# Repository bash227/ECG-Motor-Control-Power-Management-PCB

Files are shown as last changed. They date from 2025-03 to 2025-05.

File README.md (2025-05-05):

# ECG-Integrated Motor Control PCB  
**Final Project for BME405 - Introduction to Design of Medical Electronic Devices**  
*Ankara University, Department of Biomedical Engineering*  

---

## Project Overview  
A multi-functional PCB combining:  
- **ECG Signal Acquisition** (INA188 instrumentation amplifier, 0.5Hz-100Hz bandwidth)  
- **Power Management** (3.6V Li-ion charging, ±5V/12V regulation)  
- **Motor/Actuator Control** (BD6220F-E2 driver, relay circuits)  

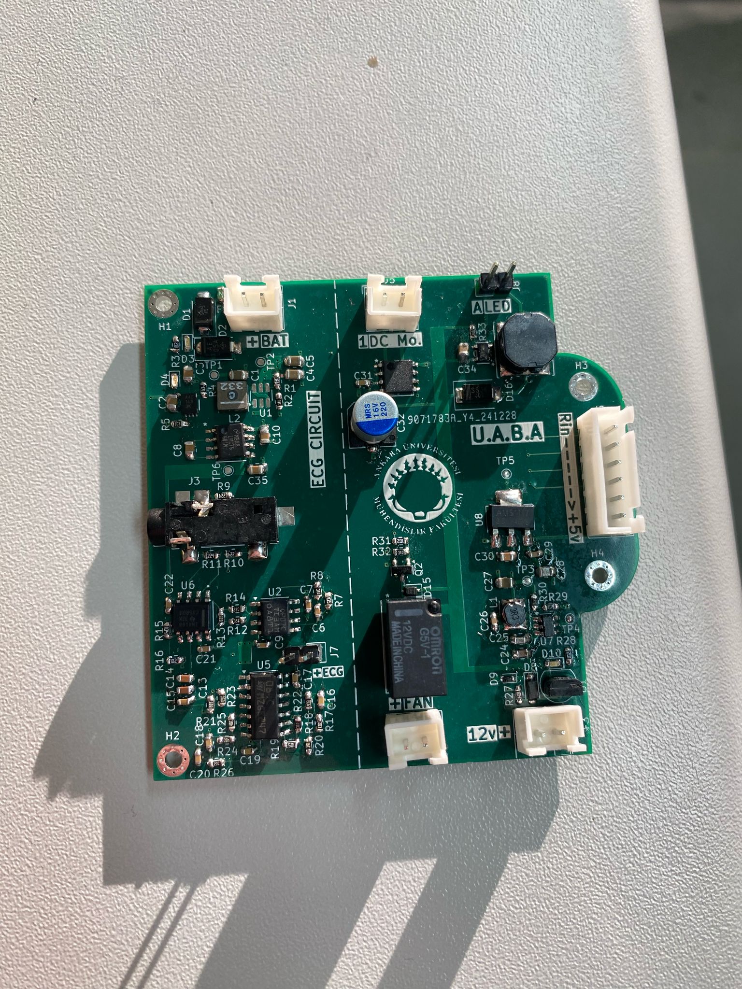
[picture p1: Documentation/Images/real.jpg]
PCB 3D Render


---

## Team Members  
| Name              | Role                                  |  
|-------------------|---------------------------------------|  
| [bash227](https://github.com/bash227)| PCB Layout              |  
| [UmutAygun](https://github.com/UmutAygun)| Schematic Design          |  

---

## Repository Structure  
```plaintext
ECG_Motor_PCB/
├── Hardware/ 
│   │   
│   ├── Outputs/
│   └── 3D models/
├── Documentation/
└── README.md
```

## Key Features
### Power managment
- MCP73831 Li-ion charger (0.5A)
- TLV61070A boost converter (3.6V→5V)
- LMC7660 voltage inverter (+5V→-5V)

### ECG Frontend
- INA188 instrumentation amplifier (G=10)
- 0.05Hz high-pass filter
- 50Hz notch filter

### Motor Control
- BD6220F-E2 DC motor driver
- AP8803WTG-7 LED driver
- Optoisolated relay control
---
##  Setup Guide
1. Clone the repository:
```bash
git clone https://github.com/yourusername/ECG-Motor-Control-PCB.git
```
2. Open in KiCad:
```bash
PCB_FINAL_UPDATED.kicad_pro
```
3. Set 3D model path in KiCad:
```bash
KICAD8_3DMODEL_DIR = ${KIPRJMOD}/Hardware/3D_Models
```
## Academic Information
- Course: BME405 - Introduction to Medical Electronics Design
- Institution: Ankara University

## License

This project is licensed under the **MIT License** - see the [LICENSE](LICENSE) file for details.

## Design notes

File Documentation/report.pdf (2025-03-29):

### 1- Soldiered circuit

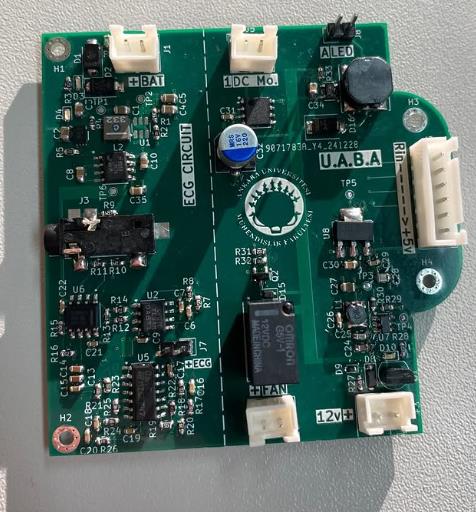
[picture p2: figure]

### 2- PCB design

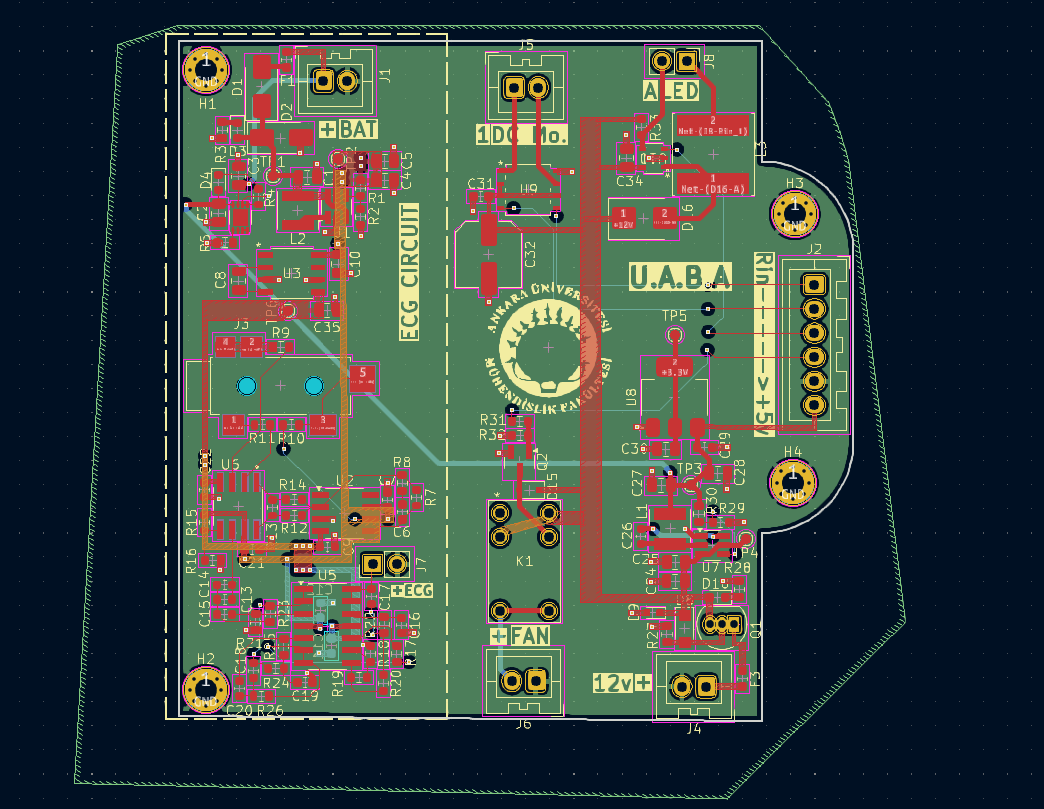
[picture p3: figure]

### 3- Schematics a- Analog circuit’s protection and regulators

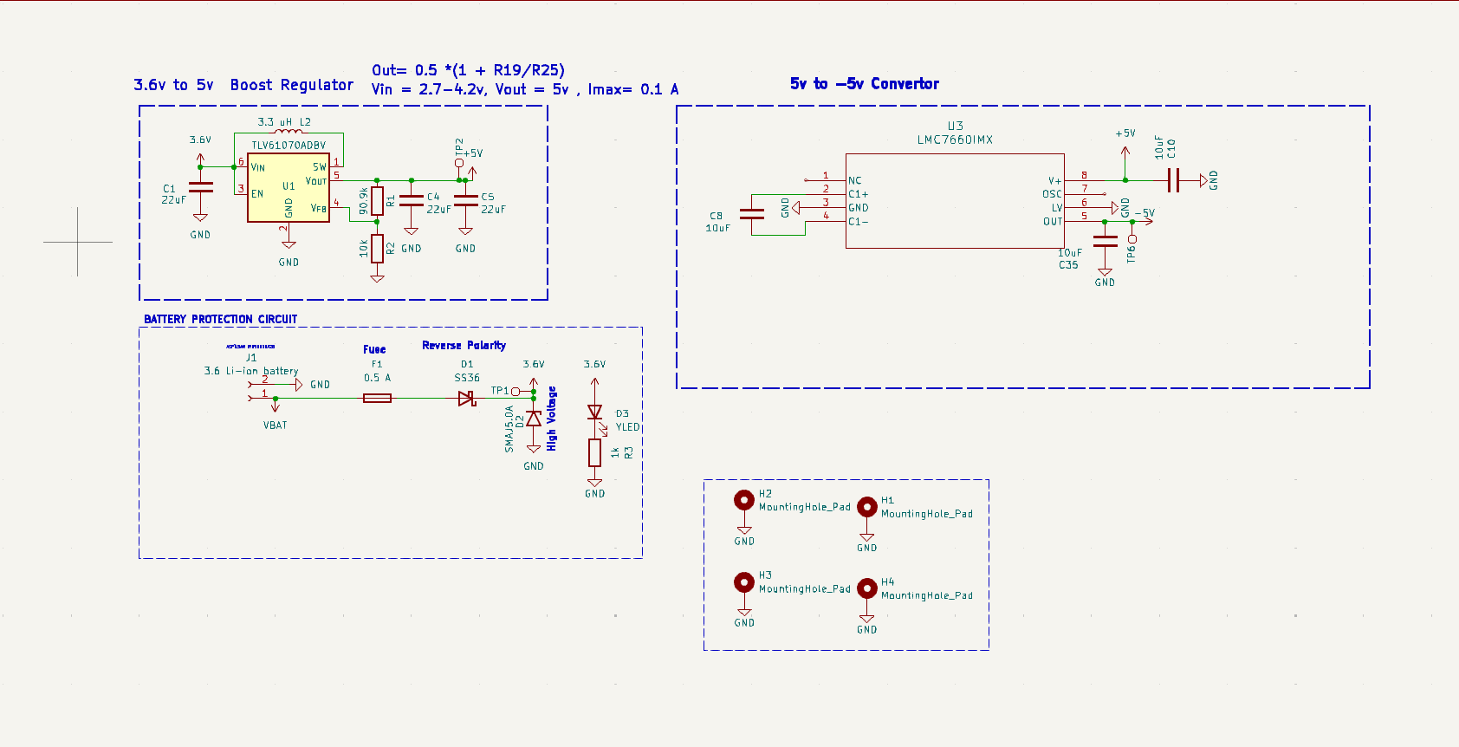
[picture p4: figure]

The battery will provide 3.6v, at first there is high current protection (F1) , reverse polarity protection (D1) and high voltage protection (D2), then the 3.6v is boosted to 5v using boost regulator (TLV61070ADBV) and the output voltage is controlled using 2 resistors (R2, R1) by using the values in the formula in the picture, because of the low values of the ECG, -5v have to be provided to the negative

### voltage pin of the amplifiers, and it’s supplied by another regulator (LMC7660IMX

### b- ECG signal amplifying circuit

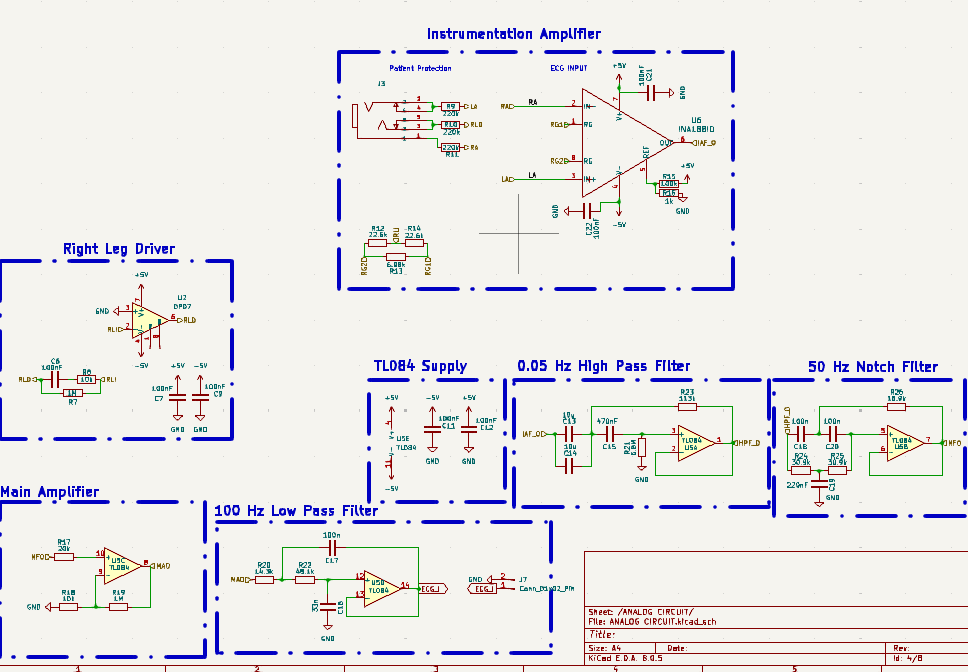
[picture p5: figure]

### Before the amplifying patient protection (using high resistance resistors to minimize the

current) and right leg driver (to eliminate the body’s noise ) are done. With a 10 gain the signal is amplified using the instrumentational amplifier (INA188ID), after that the signal is filtered by a 0.5Hz high pass filter and 50Hz notch filter, then the main amplifier amplifies the signal by a gain of 100, finally the signal is filtered using 100Hz low pass filter.

### c- Charger circuit

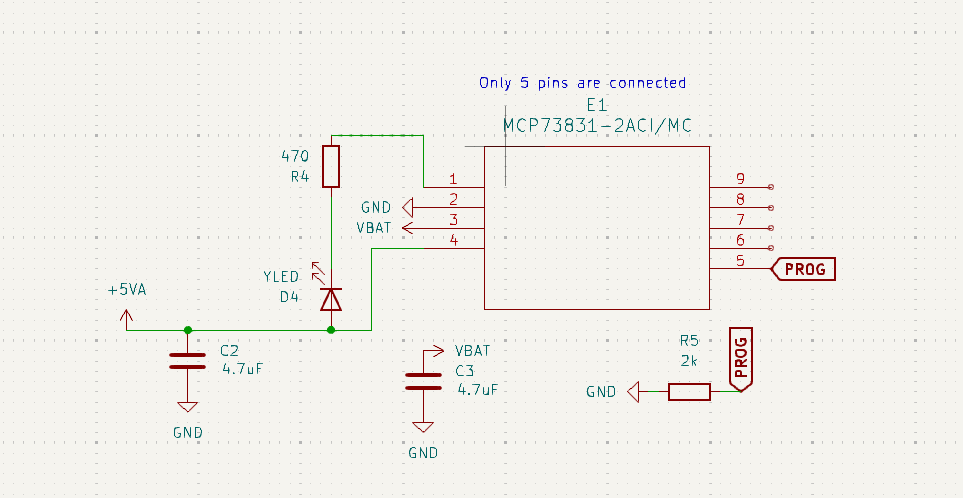
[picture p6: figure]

### To charge the battery with a charge module (MCP73831-2ACI/MC) with a 0.5A charging

current.

### d- High voltage protection and regulation circuit

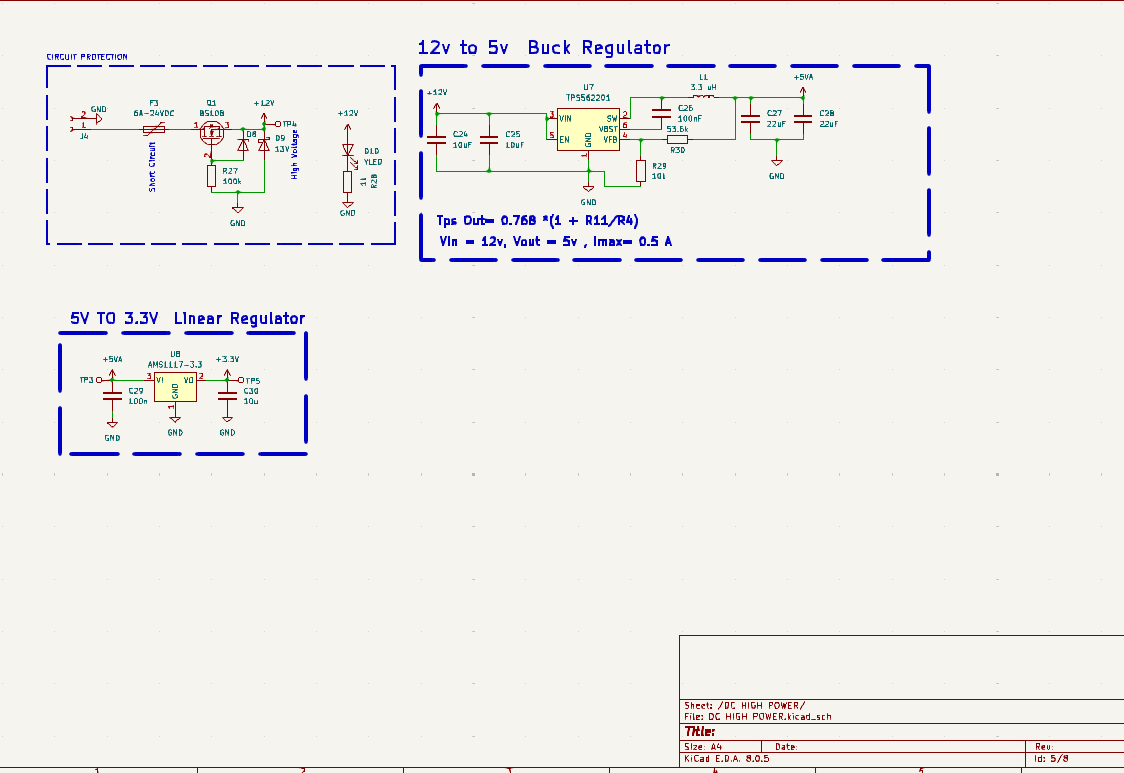
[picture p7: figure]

For the high voltage section same protection is done but due to the high current for reverse polarity protection transistor is done instead of Schottky diode. After that the 12v dc voltage is regulated to 5v using buck regulator (TPS562201), after that the 5v is regulated to 3.3v using linear regulator (AMS1117-3.3).

### e- DC motor driver and control connector

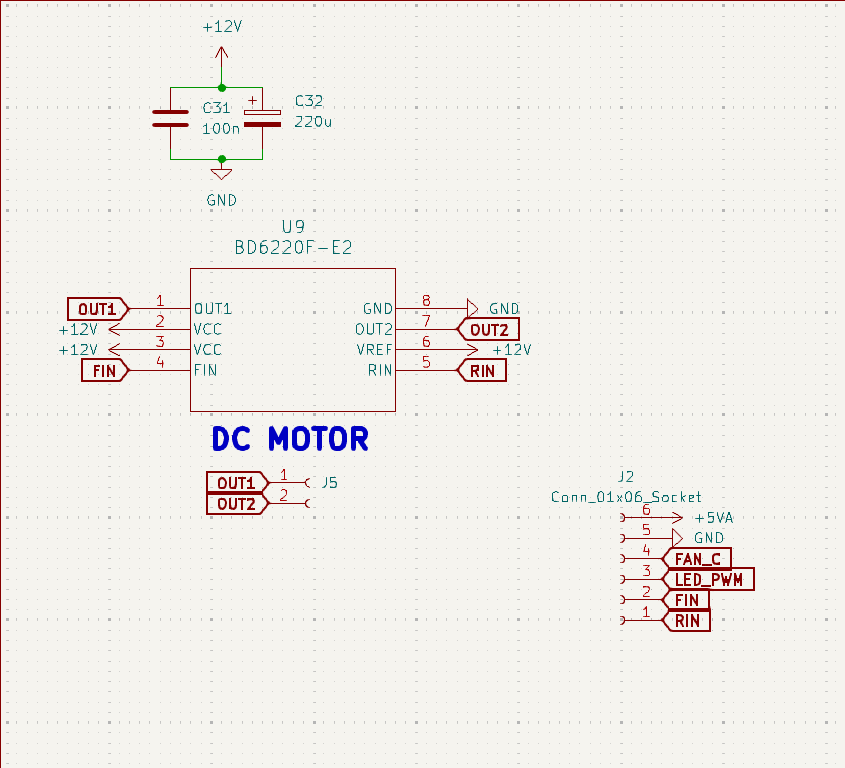
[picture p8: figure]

In here there is a dc motor driver (BD6220F-E2) and 2 decoupling capacitors connected to it, its supplied with 12v for motor supply, and the motors will be connected to OUT1 and OUT2 pins.

For the control connector there is 5v output to test the circuit and other pins for the other components control.

### f- Fan control circuit

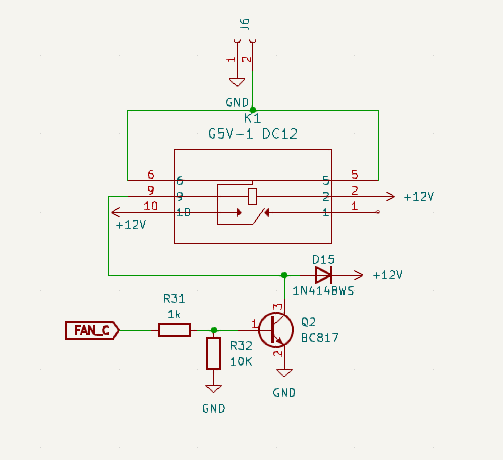
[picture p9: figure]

A relay is used with a transistor to control the fan, and a diode to block the current that is stored in the coil in the relay, and its controlled using the FAN_C pin in the control connector.

### g- Led driver circuit

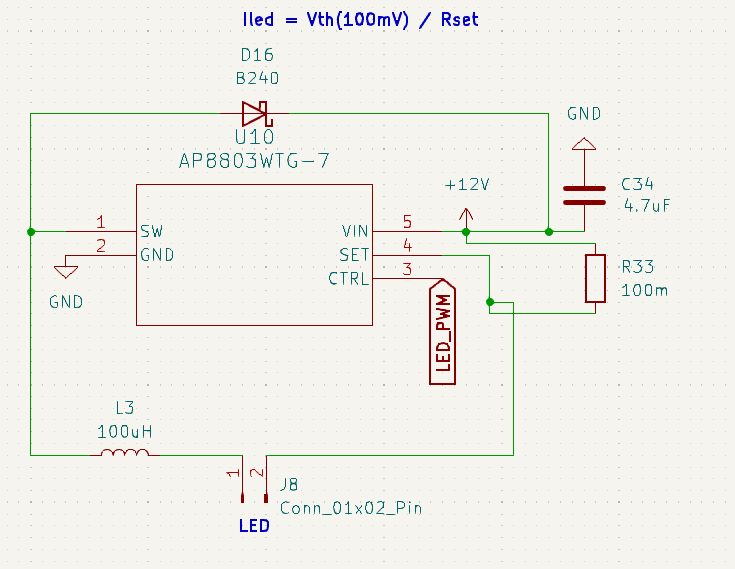
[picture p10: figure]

A led driver to control (AP8803WTG-7) the LED driver is supplied with 12v and the current is set using the R33 value so the LED current in this circuit is 1A.

### 4- BOM list

null | References | Value | Footprint | Quantity | LINK
1 | C6, C7, C9, C11, C12, C17, C18, C20, C21, C22, C26, C29, C31 | 100nF | C_0603_1608Metric | 13 | https://ozdisan.com/Product/Detail/476015/C C0603KRX7R9BB104 (https://ozdisan.com/Product/Detail/476015/CC0603KRX7R9BB104)
2 | C8, C10, C24, C25, C30, C35 | 10uF | C_0805_2012Metric | 6 | https://ozdisan.com/p/57?ids=9695;452010,9697;356027&groupids=9695,9697&propids=452010,356027&SearchText=10uf&sayfaAdedi=20
3 | C1, C4, C5, C27, C28 | 22uF | C_0805_2012Metric | 5 | https://ozdisan.com/pasif-komponentler/kapasitorler/smt-smd-ve-mlcc-kapasitorler/CL21A226MPCLRNC/522719 (https://ozdisan.com/pasif-komponentler/kapasitorler/smt-smd-ve-mlcc-kapasitorler/CL21A226MPCLRNC/522719)
4 | C2, C3, C34 | 4.7uF | C_0805_2012Metric | 3 | https://ozdisan.com/pasif-komponentler/kapasitorler/smt-smd-ve-mlcc-kapasitorler/CL21A226MPCLRNC/522719
5 | C13, C14 | 10u | C_0603_1608Metric | 2 | https://ozdisan.com/pasif-komponentler/kapasitorler/smt-smd-ve-mlcc-kapasitorler/GRT188C81C106ME13D/732963
6 | C15 | 470nF | C_0603_1608Metric | 1 | https://ozdisan.com/pasif-komponentler/kapasitorler/smt-smd-ve-mlcc-kapasitorler/CL10B474KA8NNNC/355575
7 | C16 | 33n | C_0603_1608Metric | 1 | https://ozdisan.com/pasif-komponentler/kapasitorler/smt-smd-ve-mlcc-kapasitorler/CL10B333KB8NNNC/26341
8 | C19 | 220nF | C_0603_1608Metric | 1 | CL10B224KO8NNNC (https://ozdisan.com/pasif-komponentler/kapasitorler/smt-smd-ve-mlcc-kapasitorler/CL10B224KO8NNNC/14442)
9 | C32 | 220u | C_Elec_6.3x7.7 | 1 | CD010M221E7DPKKKV00A ,
10 | R2, R8, R18, R29, R32 | 10K | R_0603_1608Metric | 5 | CRT03F7E1002 (https://ozdisan.com/pasif-komponentler/direncler/smt-smd-ve-cip-direncler/CRT03F7E1002/1054351)
11 | R3, R16, R28, R31 | 1k | R_0603_1608Metric | 4 | CRT03J7E1001 (https://ozdisan.com/pasif-komponentler/direncler/smt-smd-ve-cip-direncler/CRT03J7E1001/1054377)
12 | R9, R10, R11 | 220k | R_0603_1608Metric | 3 | RC0603JR-07220KL (https://ozdisan.com/pasif-komponentler/direncler/smt-smd-ve-cip-direncler/RC0603JR-07220KL/834868)
13 | R7, R19 | 1M | R_0603_1608Metric | 2 | RC0603JR-071ML (https://ozdisan.com/pasif-komponentler/direncler/smt-smd-ve-cip-direncler/RC0603JR-071ML/403066)
14 | R12, R14 | 22.6k | R_0603_1608Metric | 2 | 0603SAF2262T5E (https://ozdisan.com/pasif-komponentler/direncler/smt-smd-ve-cip-direncler/0603SAF2262T5E/505927)
15 | R15, R27 | 100k | R_0603_1608Metric | 2 | RC0603JR-07100KL (https://ozdisan.com/pasif-komponentler/direncler/smt-smd-ve-cip-direncler/RC0603JR-07100KL/497416)
16 | R24, R25 | 30.9k | R_0603_1608Metric | 2 | 0603SAF3092T5E (https://ozdisan.com/pasif-komponentler/direncler/smt-smd-ve-cip-direncler/0603SAF3092T5E/467401)
17 | R1 | 90.9k | R_0603_1608Metric | 1 | RC0603FR-0790K9L (https://ozdisan.com/pasif-komponentler/direncler/smt-smd-ve-cip-direncler/RC0603FR-0790K9L/618083)
18 | R4 | 470 | R_0603_1608Metric | 1 | RC0603JR-07470RL (https://ozdisan.com/pasif-komponentler/direncler/smt-smd-ve-cip-direncler/RC0603JR-07470RL/387456)
19 | R5 | 2k | R_0603_1608Metric | 1 | 0603SAJ0202T5E (https://ozdisan.com/pasif-komponentler/direncler/smt-smd-ve-cip-direncler/0603SAJ0202T5E/338094)
20 | R13 | 6.98k | R_0603_1608Metric | 1 | 0603SAF6981T5E (https://ozdisan.com/pasif-komponentler/direncler/smt-smd-ve-cip-direncler/0603SAF6981T5E/505901)
21 | R17 | 20k | R_0603_1608Metric | 1 | 0603SAJ0203T5E (https://ozdisan.com/pasif-komponentler/direncler/smt-smd-ve-cip-direncler/0603SAJ0203T5E/349000)
22 | R20 | 14.3k | R_0603_1608Metric | 1 | 0603SAF1432T5E (https://ozdisan.com/pasif-komponentler/direncler/smt-smd-ve-cip-direncler/0603SAF1432T5E/505915)
23 | R21 | 6.8M | R_0603_1608Metric | 1 | 0603SAF6804T5E (https://ozdisan.com/pasif-komponentler/direncler/smt-smd-ve-cip-direncler/0603SAF6804T5E/602901)
24 | R22 | 48.1k | R_0603_1608Metric | 1 | CRT03F7E4702 47k (https://ozdisan.com/pasif-komponentler/direncler/smt-smd-ve-cip-direncler/CRT03F7E4702/1054352)
25 | R23 | 113k | R_0603_1608Metric | 1 | 0603SAF1133T5E (https://ozdisan.com/pasif-komponentler/direncler/smt-smd-ve-cip-direncler/0603SAF1133T5E/505968)
26 | R26 | 16.9k | R_0603_1608Metric | 1 | 0603WGF1692T5E (https://ozdisan.com/pasif-komponentler/direncler/smt-smd-ve-cip-direncler/0603WGF1692T5E/335214)
27 | R30 | 53.6k | R_0603_1608Metric | 1 | 0603SAF5362T5E (https://ozdisan.com/pasif-komponentler/direncler/smt-smd-ve-cip-direncler/0603SAF5362T5E/454292)
28 | R33 | 100m | R_0603_1608Metric | 1 | 0603SAF100LT5E (https://ozdisan.com/pasif-komponentler/direncler/smt-smd-ve-cip-direncler/0603SAF100LT5E/456321)
29 | L1 | 3.3 uH | L_Wurth_WE-LQSH-4020 | 1 | FPI0302-3R3M
30 | L2 | 3.3 uH | L_Abracon_ASPI-4030S | 1 | XFL4020-332MEC
31 | L3 | 100uH | L_Changjiang_FNR8040S | 1 | SRN8040-101M
32 | D3, D4, D10 | YLED | LED_0603_1608Metric | 3 | 27-21/GHC-YR2T1/3C
33 | D1 | SS36 | D_SMA | 1 | SS36-DO214AB-HT (https://ozdisan.com/guc-yari-iletkenleri/diyotlar-modul-diyotlar-ve-dogrultucular/schottky-diyotlar/SS36-DO214AB-HT/475999)
34 | D2 | SMAJ5.0A | D_SMA | 1 | SMAJ5.0A-E3/61T (https://ozdisan.com/guc-yari-iletkenleri/diyotlar-modul-diyotlar-ve-dogrultucular/tvs-diyotlar/SMAJ5-0A-E361T/34825)
35 | D8 | 10V | Nexperia_CFP3_SOD-123W | 1 | MMSZ10V-HT

36 | D9 | 13V | D_SOD-523 | 1 | BZT52B13T-HT
37 | D15 | 1N4148WS | D_SOD-323 | 1 | 1N4148WS_R1_00001 (https://ozdisan.com/guc-yari-iletkenleri/diyotlar-modul-diyotlar-ve-dogrultucular/genel-amacli-diyotlar/1N4148WSR100001/509214)
38 | D16 | B240 | D_SMB | 1 | SS26-E3/52T (https://ozdisan.com/guc-yari-iletkenleri/diyotlar-modul-diyotlar-ve-dogrultucular/schottky-diyotlar/SS26-E352T/368413)
39 | U1 | TLV61070ADBV | SOT-23-6 | 1
40 | U2 | OP07 | SO-8_3.9x4.9mm_P1.27mm | 1 | OP07CDR
41 | U3 | LMC7660IMX | M08A_TEX | 1 | LMC7660IMX (https://ozdisan.com/entegre-devreler-icler/guc-entegreleri/dc-dc-voltaj-regulatorleri/LMC7660IMX/41100)
42 | U5 | TL084 | SOIC-14_3.9x8.7mm_P1.27mm | 1 | TL084CDT (https://ozdisan.com/entegre-devreler-icler/lineer-entegreler/amplifikatorler/TL084CDT/12815)
43 | U6 | INA188ID | INA188ID | 1 | INA188IDR (https://ozdisan.com/entegre-devreler-icler/lineer-entegreler/amplifikatorler/INA188IDR/527318)
44 | U7 | TPS562201 | SOT-23-6 | | TPS562201DDCR (https://ozdisan.com/entegre-devreler-icler/guc-entegreleri/dc-dc-voltaj-regulatorleri/TPS562201DDCR/708034)
45 | U8 | AMS1117-3.3 | SOT-223-3_TabPin2 | 1 | AMS1117-3.3 (https://ozdisan.com/entegre-devreler-icler/guc-entegreleri/lineer-voltaj-regulatorleri/AMS1117-3-3/348307)
46 | U9 | BD6220F-E2 | SOP8_ROM-L | 1 | BD6220F-E2
47 | U10 | AP8803WTG-7 | TSOT25-WT_DIO-L | 1 | AP8803WTG-7
48 | F1 | 0.5 A | Fuse_0603_1608Metric | 1 | SF-0603SP050-2
49 | F3 | 6A-24VDC | Fuse_0603_1608Metric | 1 | 3412.0119.22 (https://ozdisan.com/devre-koruyucular/sigorta-bilesenleri/sigortalar/3412-0119-22/634995)
50 | TP1, TP2, TP3, TP4, TP5, TP6 | TestPoint | TestPoint_Pad_D1.0mm | 6
51 | E1 | MCP73831-2ACI/MC | DFN8_2x3MC_MCH-L | 1 | MCP73831-2ACI/MC
52 | K1 | G5V-1 DC12 | G5V_1 | 1 | G5V-1-DC12 (https://ozdisan.com/elektromekanik-komponentler/roleler-ve-role-soketleri/genel-tip-roleler/G5V-1-DC12/472483)
53 | Q1 | BS108 | TO-92_Inline | 1 | ZVP3304A (https://ozdisan.com/guc-yari-iletkenleri/mosfetler/discrete-mosfetler/ZVP3304A/9153)
54 | Q2 | BC817 | SOT-23 | 1 | BC817-40-TP (https://ozdisan.com/guc-yari-iletkenleri/transistorler/discrete-transistorler/BC817-40-TP/600305)
55 | J4, J5, J6 | Conn_01x02_Socket | JST_XA_B02B-XASK-1_1x02_P2.50mm_Vertical | 3 | L-KLS1-2.50-02-H (https://ozdisan.com/konnektor-ve-baglanti-elemanlari/konnektor-cesitleri/housing-konnektorler/L-KLS1-2-50-02-H/456055)
56 | J7, J8 | Conn_01x02_Pin | PinHeader_1x02_P2.54mm_Ve rtical | 2 | L-KLS1-207-1-02-S
57 | J1 | 3.6 Li-ion battery | JST_XA_B02B-XASK-1_1x02_P2.50mm_Vertical | 1 | L-KLS1-2.50-02-H (https://ozdisan.com/konnektor-ve-baglanti-elemanlari/konnektor-cesitleri/housing-konnektorler/L-KLS1-2-50-02-H/456055)
58 | J2 | Conn_01x06_Socket | JST_XA_B06B-XASK-1_1x06_P2.50mm_Vertical | 1 | L-KLS1-2.50-06-S
59 | J3 | 35RASMT4BHNTRX | 35RASMT4BHNTRX | 1 | L-KLS1-TPJ3.5-002C

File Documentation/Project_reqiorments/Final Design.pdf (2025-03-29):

## Final Design

## Battery Powered Analog Section

1. Design battery boost circuit 3.6v to 5 and 5 to -5v,
- Add connector for input;
- Add circuit protections;
- Add test point of all voltages

### 2. Design 0.5 A battery charger circuit

3. Design ECG Analog front end;
- Add test point of analog front end output
- you can use LMC7660 insted of LM2776 and INA188 instead of AD620

### 4. add battery input connector and 5v input connector for battery charger

## DC High Power Section

1.Design 12v to 5v buck convertor ,5v to 3.3v linear regulator

- Add connector for 12v input;
- Add circuit protections;(reverse polarity with p channel mosfet)
- Add test point of all voltages

### 2. Design 12 v 0.5A Dc motor driver(add motor connector)

### 3. Design 12 v 1A Relay circuit(add connector for relay)

### 4. Design 12v 1A led driver(add connector for led)

Add test point or header to control dc motor, relay circuit and led driver

*Design 4 layer Pcb(signal-gnd-power-signal)

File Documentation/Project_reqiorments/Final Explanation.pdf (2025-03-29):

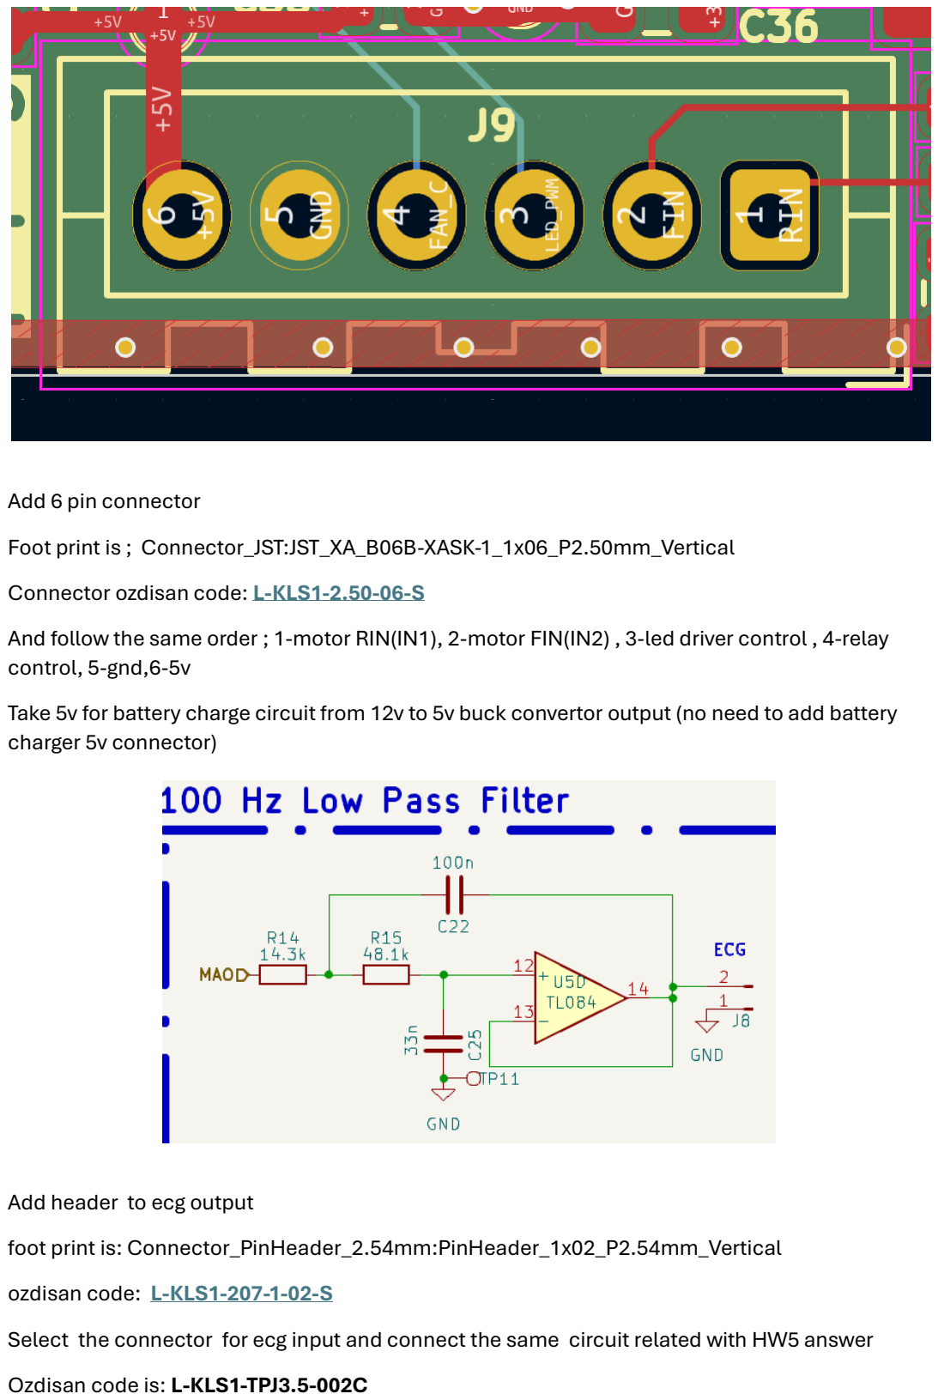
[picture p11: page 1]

Add 6 pin connector
Foot print is ; Connector_JST:JST_XA_B06B-XASK-1_1x06_P2.50mm_Vertical
Connector ozdisan code: L-KLS1-2.50-06-S (https://ozdisan.com/konnektor-ve-baglanti-elemanlari/konnektor-cesitleri/pcb-konnektorler/L-KLS1-2-50-06-S/457970)
And follow the same order ; 1-motor RIN(IN1), 2-motor FIN(IN2) , 3-led driver control , 4-relay control, 5-gnd,6-5v
Take 5v for battery charge circuit from 12v to 5v buck convertor output (no need to add battery charger 5v connector)

Add header to ecg output
foot print is: Connector_PinHeader_2.54mm:PinHeader_1x02_P2.54mm_Vertical ozdisan code: L-KLS1-207-1-02-S (https://ozdisan.com/konnektor-ve-baglanti-elemanlari/header-konnektorler/pin-headerlar/L-KLS1-207-1-02-S/464873)
Select the connector for ecg input and connect the same circuit related with HW5 answer Ozdisan code is: L-KLS1-TPJ3.5-002C

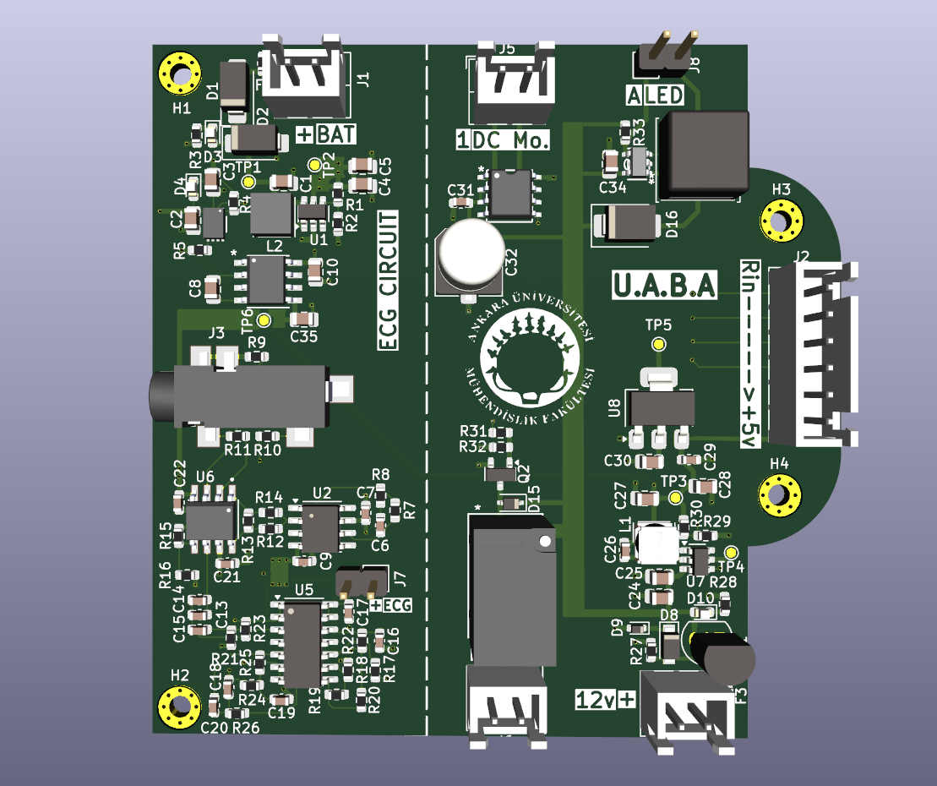
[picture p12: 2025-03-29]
Documentation/Images/PCB_FINAL_UPDATED.png

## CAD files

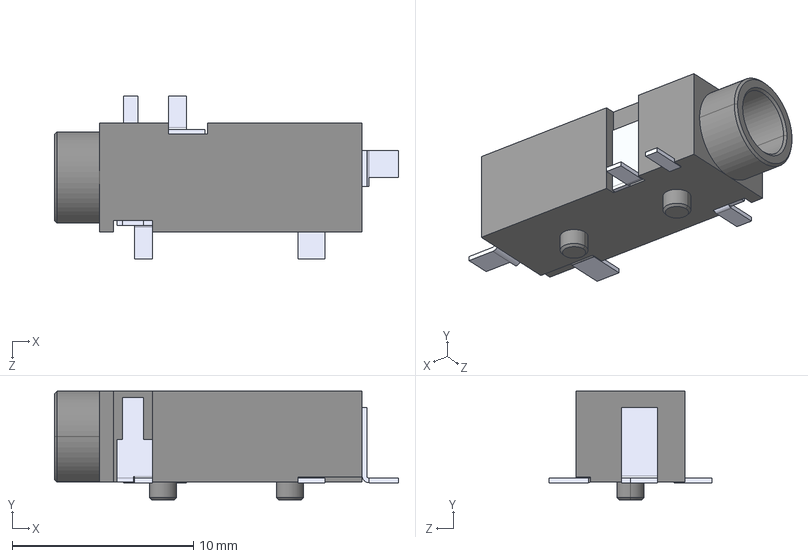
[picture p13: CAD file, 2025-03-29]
Hardware/3d models/35RASMT4BHNTRX.STEP
19.0 x 5.99 x 8.99 mm

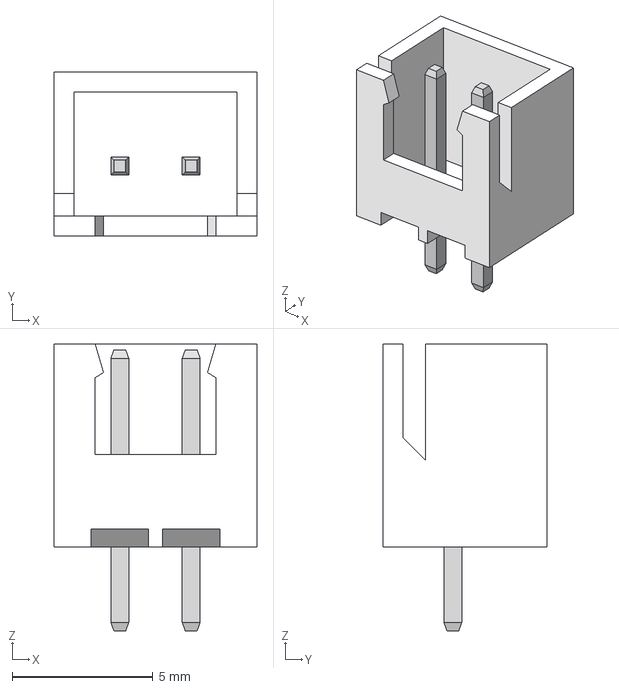
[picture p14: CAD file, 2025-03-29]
Hardware/3d models/JST - XH - Thru (V) - 2Pin - 2.54mm.stp
7.21 x 5.84 x 10.2 mm

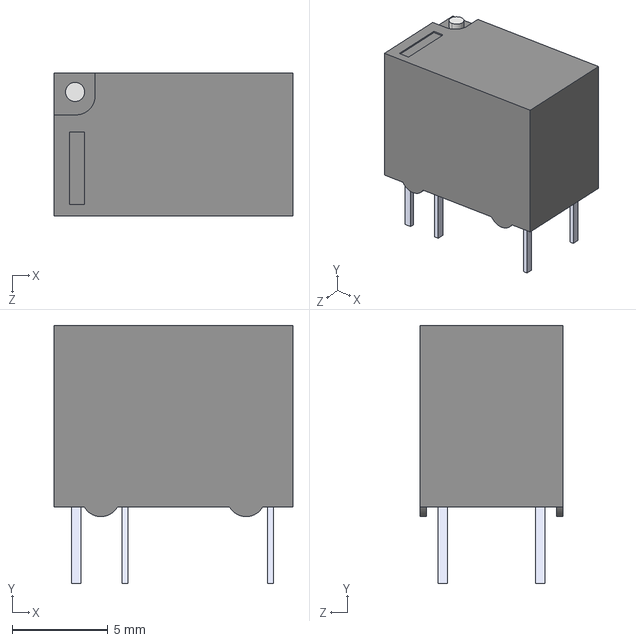
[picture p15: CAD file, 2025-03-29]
Hardware/3d models/G5V-1 DC12.STEP
12.5 x 13.5 x 7.50 mm

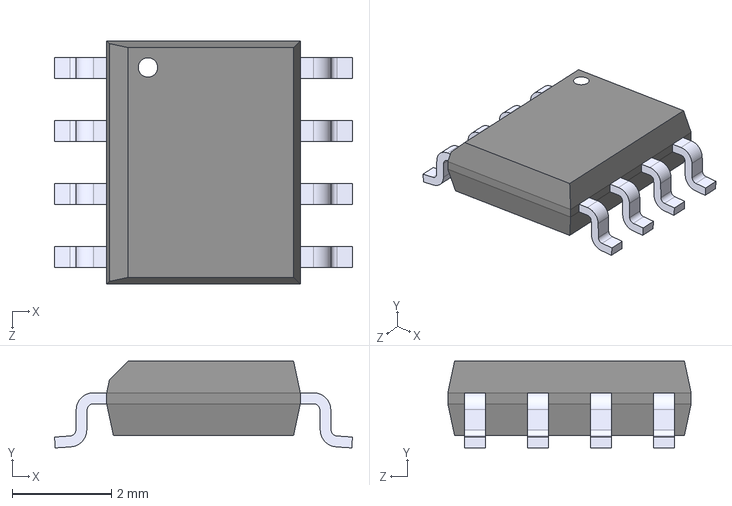
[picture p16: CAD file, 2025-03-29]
Hardware/3d models/INA188ID.step
6.00 x 1.75 x 4.90 mm

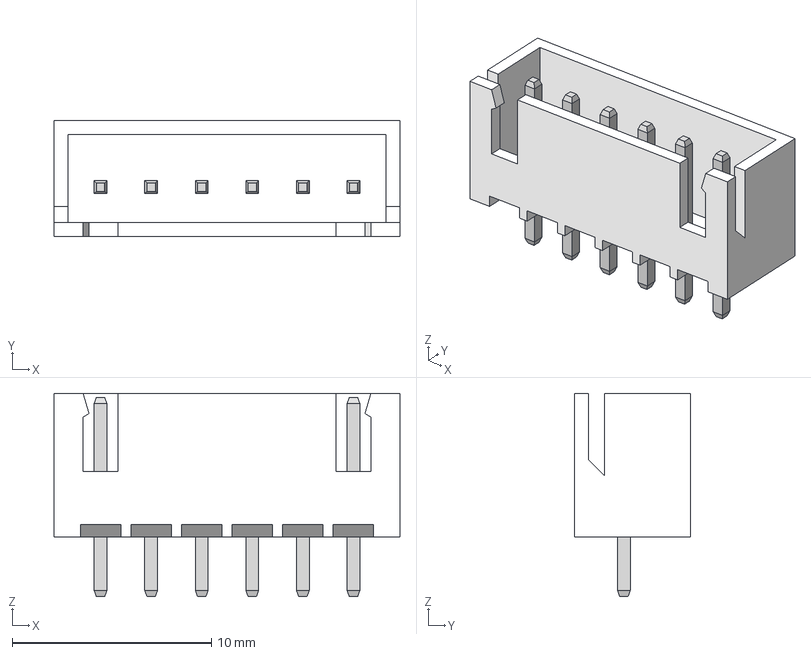
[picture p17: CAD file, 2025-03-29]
Hardware/3d models/JST - XH - Thru (V) - 6Pin - 2.54mm.stp
17.4 x 5.84 x 10.2 mm

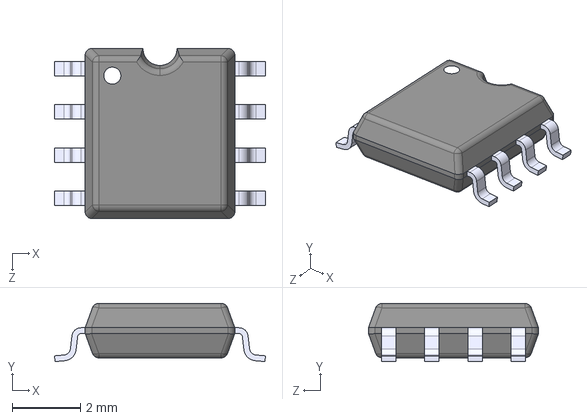
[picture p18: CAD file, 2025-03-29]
Hardware/3d models/BD6220F-E2.step
6.20 x 1.71 x 5.00 mm

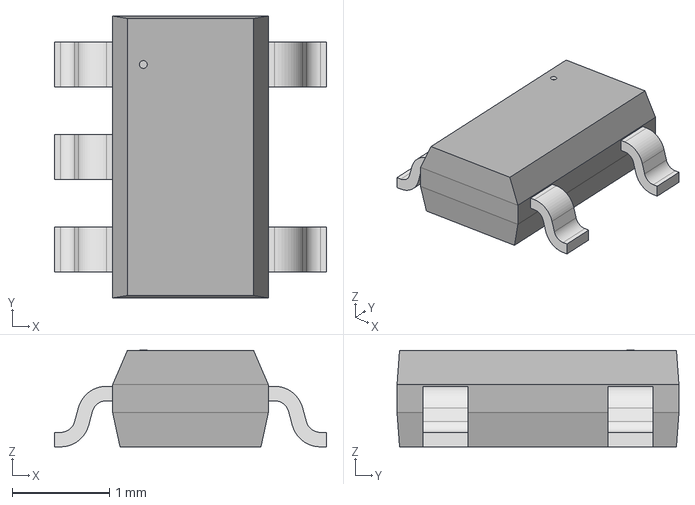
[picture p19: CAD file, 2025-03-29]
Hardware/3d models/AP8803WTG_7.step
2.79 x 2.90 x 0.993 mm

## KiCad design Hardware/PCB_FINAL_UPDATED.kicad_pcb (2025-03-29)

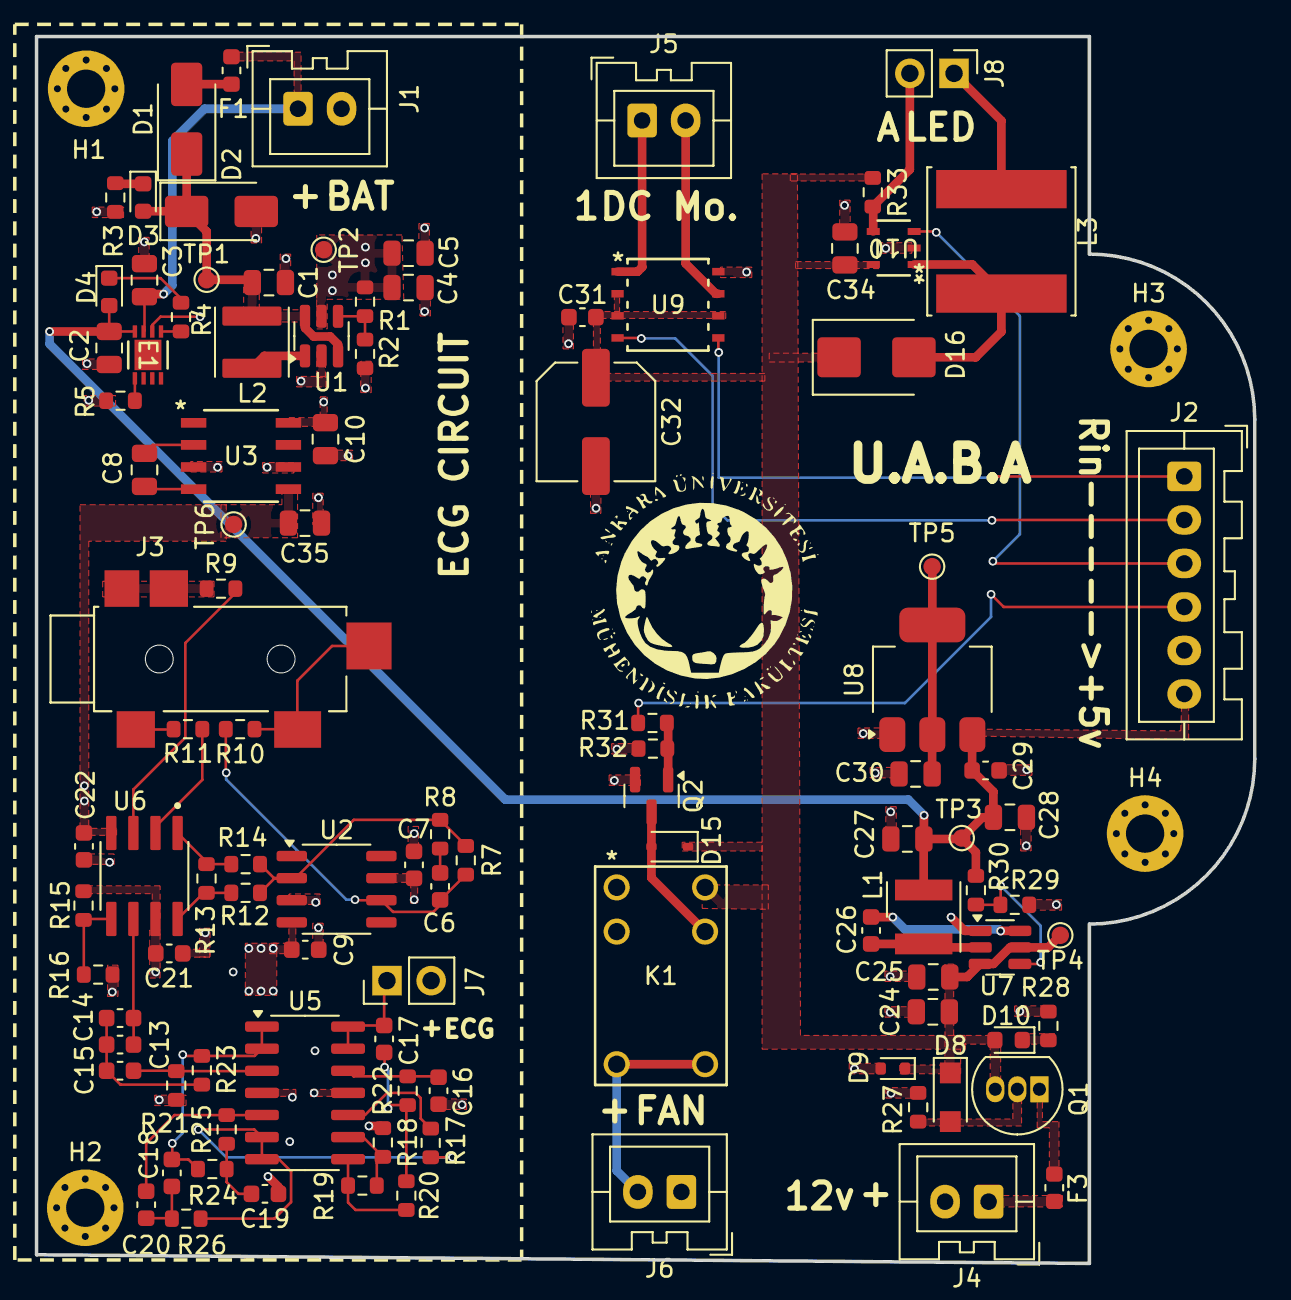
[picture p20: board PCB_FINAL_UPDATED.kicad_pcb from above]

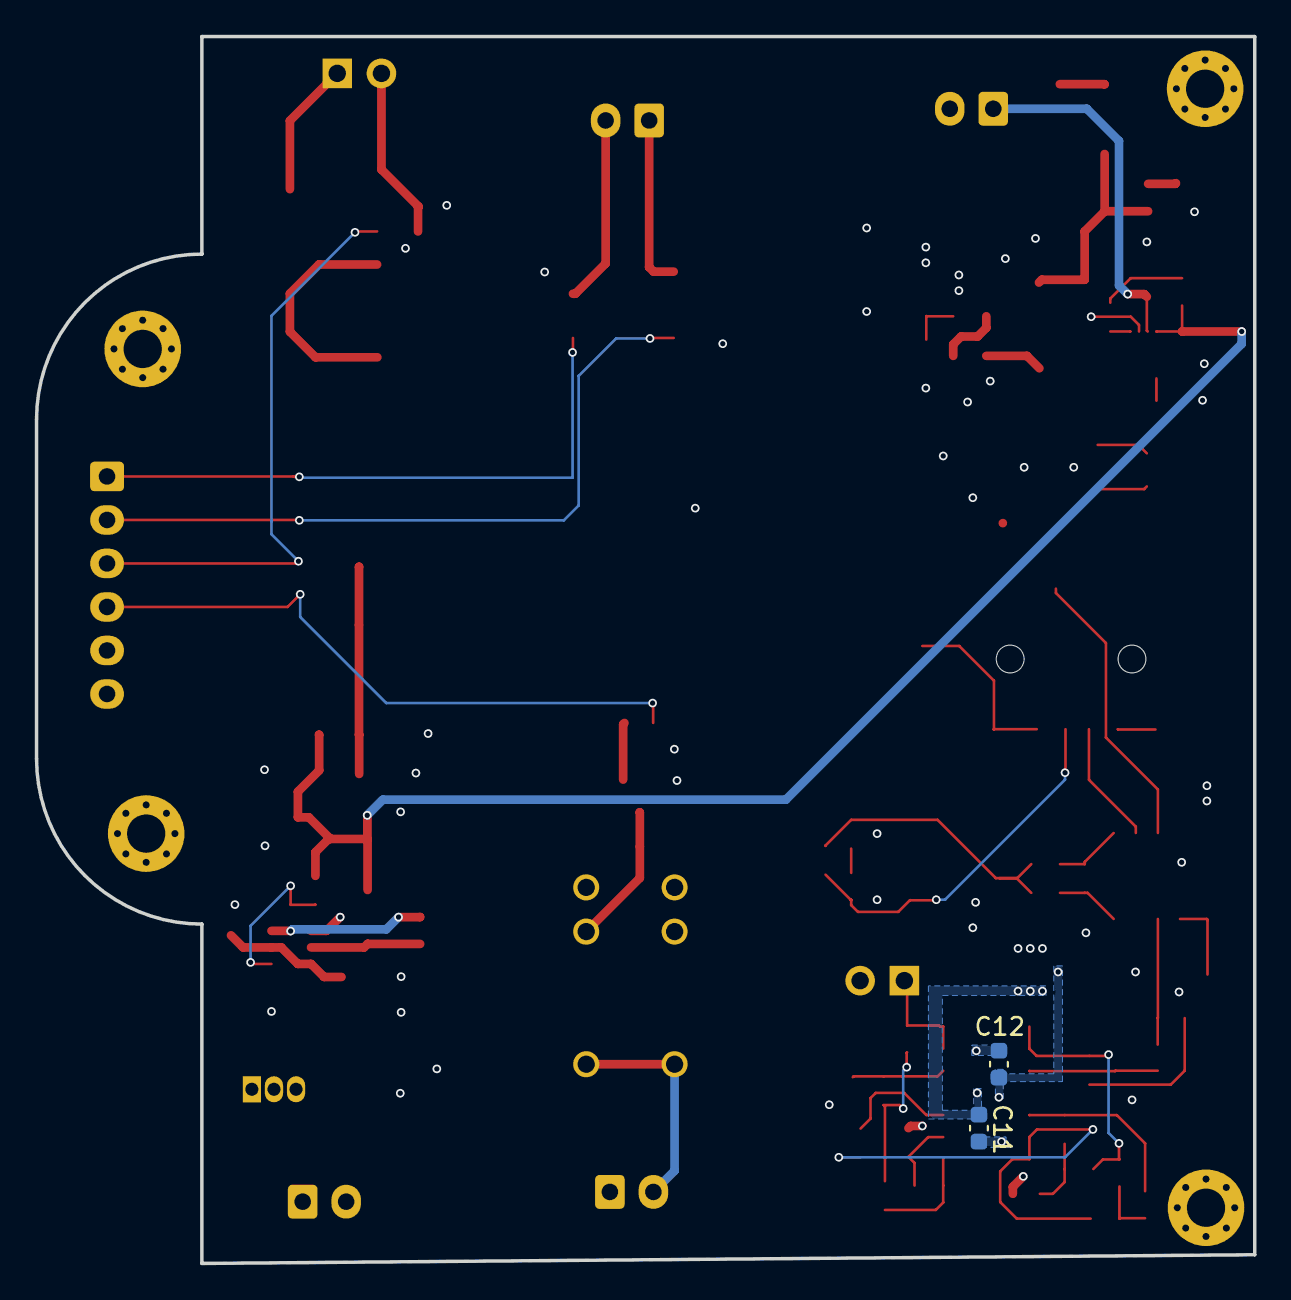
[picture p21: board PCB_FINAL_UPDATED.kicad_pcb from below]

Board: 4 copper layers, 70.0 x 70.5 mm, 110 parts (2 on the bottom side), 61 nets.

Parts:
C1, C4, C5, C27, C28: 22uF; C_0805_2012Metric
C2, C3, C34: 4.7uF; C_0805_2012Metric
C6, C7, C9, C11, C12, C21, C22, C26: 100nF; C_0603_1608Metric
C8, C10, C24, C25, C35: 10uF; C_0805_2012Metric
C13, C14: 10u; C_0603_1608Metric
C15: 470nF; C_0603_1608Metric
C16: 33n; C_0603_1608Metric
C17, C18, C20, C29, C31: 100n; C_0603_1608Metric
C19: 220nF; C_0603_1608Metric
C30: 10u; C_0805_2012Metric
C32: 220u; C_Elec_6.3x7.7
D1: SS36; D_SMA
D2: SMAJ5.0A; D_SMA
D3, D4, D10: YLED; LED_0603_1608Metric
D8: 10V; Nexperia_CFP3_SOD-123W
D9: 13V; D_SOD-523
D15: 1N4148WS; D_SOD-323
D16: B240; D_SMB
E1: MCP73831-2ACI/MC; DFN8_2x3MC_MCH-L
F1: 0.5 A; Fuse_0603_1608Metric
F3: 6A-24VDC; Fuse_0603_1608Metric
H1, H2, H3, H4: MountingHole_Pad; MountingHole_2.2mm_M2_Pad_Via
J1: 3.6 Li-ion battery; JST_XA_B02B-XASK-1_1x02_P2.50mm_Vertical
J2: Conn_01x06_Socket; JST_XA_B06B-XASK-1_1x06_P2.50mm_Vertical
J3: 35RASMT4BHNTRX
J4, J5, J6: Conn_01x02_Socket; JST_XA_B02B-XASK-1_1x02_P2.50mm_Vertical
J7, J8: Conn_01x02_Pin; PinHeader_1x02_P2.54mm_Vertical
K1: G5V-1 DC12; G5V_1
L1: 3.3 uH; L_Wurth_WE-LQSH-4020
L2: 3.3 uH; L_Abracon_ASPI-4030S
L3: 100uH; L_Changjiang_FNR8040S
Q1: BS108; TO-92_Inline
Q2: BC817; SOT-23
R1: 90.9k; R_0603_1608Metric
R2, R8, R18, R29: 10k; R_0603_1608Metric
R3, R16, R28, R31: 1k; R_0603_1608Metric
R4: 470; R_0603_1608Metric
R5: 2k; R_0603_1608Metric
R7, R19: 1M; R_0603_1608Metric
R9, R10, R11: 220k; R_0603_1608Metric
R12, R14: 22.6k; R_0603_1608Metric
R13: 6.98k; R_0603_1608Metric
R15, R27: 100k; R_0603_1608Metric
R17: 20k; R_0603_1608Metric
R20: 14.3k; R_0603_1608Metric
R21: 6.8M; R_0603_1608Metric
R22: 48.1k; R_0603_1608Metric
R23: 113k; R_0603_1608Metric
R24, R25: 30.9k; R_0603_1608Metric
R26: 16.9k; R_0603_1608Metric
R30: 53.6k; R_0603_1608Metric
R32: 10K; R_0603_1608Metric
R33: 100m; R_0603_1608Metric
TP1, TP2, TP3, TP4, TP5, TP6: TestPoint; TestPoint_Pad_D1.0mm
U1: TLV61070ADBV; SOT-23-6
U2: OP07; SO-8_3.9x4.9mm_P1.27mm
U3: LMC7660IMX; M08A_TEX
U5: TL084; SOIC-14_3.9x8.7mm_P1.27mm
U6: INA188ID
U7: TPS562201; SOT-23-6
U8: AMS1117-3.3; SOT-223-3_TabPin2
U9: BD6220F-E2; SOP8_ROM-L
U10: AP8803WTG-7; TSOT25-WT_DIO-L

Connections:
3.6V: C1.1, D1.1 (K), D2.1 (A1), D3.2 (A), L2.1, TP1.1, U1.3 (EN), U1.6 (V_{IN})
+3.3V: C30.1, TP5.1, U8.2 (VO)
+5V: C4.1, C5.1, C7.1, C10.2, C12.1, C21.1, R1.2, R15.2, TP2.1, U1.5 (V_{OUT}), U2.7 (V+), U3.8 (V+), U5.4 (V+), U6.7 (V+)
+5VA: C2.1, C27.1, C28.1, C29.1, D4.2 (A), E1.4, J2.6, L1.2, R30.2, TP3.1, U8.3 (VI)
+12V: C24.1, C25.1, C31.1, C32.1, C34.2, D8.1 (K), D9.1 (K), D10.2 (A), D15.1 (K), D16.1 (K), K1.2, K1.10, Q1.3 (S), R33.1, TP4.1, U7.3 (VIN), U7.5 (EN), U9.2 (VCC), U9.3 (VCC), U9.6 (VREF), U10.5 (VIN)
-5V: C9.1, C11.1, C22.1, C35.2, TP6.1, U2.4 (V-), U3.5 (OUT), U5.11 (V-), U6.4 (V-)
/ANALOG CIRCUIT/HPF_O: C18.1, R23.2, R24.1, U5.1, U5.2 (-)
/ANALOG CIRCUIT/IAF_O: C13.1, C14.1, U6.6 (OUT)
/ANALOG CIRCUIT/LA: R9.2, U6.3 (IN+)
/ANALOG CIRCUIT/MAO: R19.2, R20.1, U5.8
/ANALOG CIRCUIT/NFO: R17.1, R26.2, U5.6 (-), U5.7
/ANALOG CIRCUIT/RA: R11.2, U6.2 (IN-)
/ANALOG CIRCUIT/RG1: R13.2, R14.2, U6.1 (RG)
/ANALOG CIRCUIT/RG2: R12.1, R13.1, U6.8 (RG)
/ANALOG CIRCUIT/RLD: C6.1, R7.1, R10.2, U2.6
/ANALOG CIRCUIT/RLI: R7.2, R8.2, R12.2, R14.1, U2.2 (-)
ECG_I: C17.2, J7.1, U5.13 (-), U5.14
FAN_C: J2.4, R31.1
FIN: J2.2, U9.4 (FIN)
GND: C1.2, C2.2, C3.2, C4.2, C5.2, C7.2, C9.2, C10.1, C11.2, C12.2, C16.1, C19.1, C21.2, C22.2, C24.2, C25.2, C27.2, C28.2, C29.2, C30.2, C31.2, C32.2, C34.1, C35.1, D2.2 (A2), D9.2 (A), E1.2, H1.1, H2.1, H3.1, H4.1, J1.2, J2.5, J4.2, J6.1, J7.2, Q2.2 (E), R2.1, R3.2, R5.2, R16.2, R18.1, R21.1, R27.2, R28.2, R29.2, R32.2, U1.2 (GND), U2.3 (+), U3.3 (GND), U3.6 (LV), U7.1 (GND), U8.1 (GND), U9.8 (GND), U10.2 (GND)
LED_PWM: J2.3, U10.3 (CTRL)
unnamed: C6.2, R8.1
unnamed: C13.2, C14.2, C15.1, R23.1
unnamed: C17.1, R20.2, R22.1
unnamed: C18.2, C20.1, R26.1
unnamed: C19.2, R24.2, R25.1
unnamed: D1.2 (A), F1.2
unnamed: D3.1 (K), R3.1
unnamed: D4.1 (K), R4.1
unnamed: D8.2 (A), Q1.2 (G), R27.1
unnamed: D10.1 (K), R28.1
unnamed: D15.2 (A), K1.9, Q2.3 (C)
unnamed: D16.2 (A), L3.1, U10.1 (SW)
unnamed: E1.1, R4.2
unnamed: J3.1, R11.1
unnamed: J3.2, J3.4, R9.1
unnamed: J3.3, J3.5, R10.1
unnamed: F3.1, J4.1
unnamed: J6.2, K1.5, K1.6
unnamed: J8.1, L3.2
unnamed: J8.2, R33.2, U10.4 (SET)
unnamed: F3.2, Q1.1 (D)
unnamed: Q2.1 (B), R31.2, R32.1
unnamed: L2.2, U1.1 (SW)
unnamed: R1.1, R2.2, U1.4 (V_{FB})
unnamed: C8.1, U3.2 (C1+)
unnamed: C8.2, U3.4 (C1-)
unnamed: C15.2, R21.2, U5.3 (+)
unnamed: C20.2, R25.2, U5.5 (+)
unnamed: R17.2, U5.10 (+)
unnamed: R18.2, R19.1, U5.9 (-)
unnamed: C16.2, R22.2, U5.12 (+)
unnamed: R15.1, R16.1, U6.5 (REF)
unnamed: C26.1, L1.1, U7.2 (SW)
unnamed: C26.2, U7.6 (VBST)
unnamed: R29.1, R30.1, U7.4 (VFB)
OUT1: J5.1, U9.1 (OUT1)
OUT2: J5.2, U9.7 (OUT2)
PROG: E1.5, R5.1
RIN: J2.1, U9.5 (RIN)
VBAT: C3.1, E1.3, F1.1, J1.1
